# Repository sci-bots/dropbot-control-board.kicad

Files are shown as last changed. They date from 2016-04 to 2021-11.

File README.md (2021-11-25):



# DropBot v3 control board

The control board is a component of the [DropBot system][dropbot] responsible for:

* serial communication with the host computer (via USB)
* generation of the high-voltage driving signal (up to 140V @ < 10 kHz)
* impedance-measurement (for estimating drop position, velocity, etc.)
* control of other system hardware (e.g., switching boards)

For more information, please visit https://sci-bots.com

[Sci-Bots logo][sci-bots]

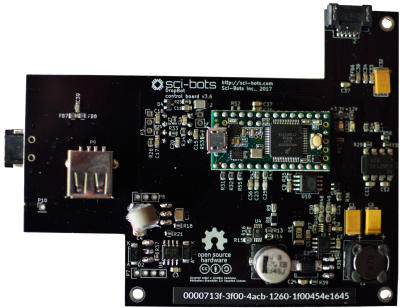
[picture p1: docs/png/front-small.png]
front

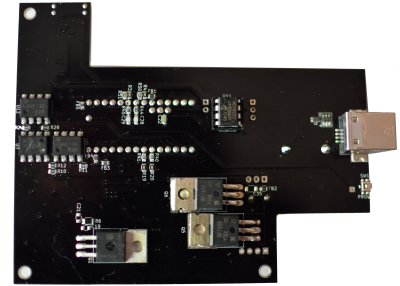
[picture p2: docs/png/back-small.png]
back


This design is open-source hardware released under a [Creative Commons Attribution-ShareAlike licence][cc-by-sa].

[][cc-by-sa]

[dropbot]: https://github.com/sci-bots/dropbot-v3
[sci-bots]: https://sci-bots.com/
[cc-by-sa]: http://creativecommons.org/licenses/by-sa/3.0

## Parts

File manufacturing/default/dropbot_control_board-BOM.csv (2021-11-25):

Refs | Quantity | MPN | Manufacturer | datasheet | footprint | value
C1 | 1 | T494D106M025AT | KEMET |  | Capacitors_Tantalum_SMD:TantalC_SizeD_EIA-7343_Reflow | 10uF
C11, C15 | 2 | CC0805KKX7R9BB105 | Yageo |  | Capacitors_SMD:C_0805 | 1uF
C12 | 1 | CL21C100JECNNWC | Samsung |  | Capacitors_SMD:C_0805 | 10pF
C13, C19-C21 | 4 | CL21C101JECNNWC | Samsung |  | Capacitors_SMD:C_0805 | 100pF
C14 | 1 | CL21C471JDFNNWG | Samsung |  | Capacitors_SMD:C_0805 | 470pF
C16 | 1 | 08053C154JAT2A | KYOCERA AVX |  | Capacitors_SMD:C_0805 | 0.15uF
C2, C3, C5, C8, C9, C17, C18, C22, C26, C33, C36-C39 | 14 | CL21B104KBCNNNC | Samsung |  | Capacitors_SMD:C_0805 | 0.1uF
C23, C25, C28-C31 | 6 | CL21C151JBANNNC | Samsung |  | Capacitors_SMD:C_0805 | 150pF
C24 | 1 | 501R15W102KV4E | Johanson |  | Capacitors_SMD:C_0805 | 1000pF
C27, C34 | 2 | CC0805KRX7R9BB103 | Yageo |  | Capacitors_SMD:C_0805 | 0.01uF
C32 | 1 | T491D336K020AT | KEMET |  | Sci-Bots:SM2917 | 33uF
C35 | 1 | DNP | DNP |  | Capacitors_SMD:C_1206 | C
C4, C10 | 2 | C1210C104KCRACTU | KEMET |  | Capacitors_SMD:C_1210 | 100n,500V
C6 | 1 | T491X107K025AT | KEMET |  | Capacitors_Tantalum_SMD:TantalC_SizeE_EIA-7360_Reflow | 100uF
C7 | 1 | EEV-EB2G3R3Q | Panasonic |  | Capacitors_SMD:c_elec_10x10 | 3.3uF,400V
D1 | 1 | VS-4EGU06-M3/5BT | Vishay |  | Diodes_SMD:SMC_Standard | 400V, 4A, <50ns
D2, D3 | 2 | US1J-13-F | Diodes Inc. |  | Diodes_SMD:SMA_Standard | D
D4 | 1 | TBAV99,LM | Toshiba |  | TO_SOT_Packages_SMD:SOT-23 | BAV99
D5 | 1 | 824015 | Würth Elektronik |  | Sci-Bots:wurth-WE-TVS_SOT23-6L | WE-TVS_824015
F1 | 1 | B59773B0120A070 | EPCOS |  | Resistors_ThroughHole:Resistor_Vertical_RM5mm | PTC
F2 | 1 | B59807A0090A062 | EPCOS |  | Resistors_SMD:R_1210 | PTC 15mA
FB1-FB8 | 8 | 742792040 | Würth Elektronik |  | Resistors_SMD:R_0805 | FERRITE
L1 | 1 | SRR1210-470M | Bourns |  | footprints:SRR1210 | 47uH,3.8A
L2 | 1 | 744231091 | Würth Elektronik |  | Sci-Bots:wurth-WE-CNSW_0805 | 90 Ohm@100MHz
LED1 | 1 | 150080BS75000 | Würth Elektronik |  | LEDs:LED_0805 | +3.3V
LED2 | 1 | 150080BS75000 | Würth Elektronik |  | LEDs:LED_0805 | +12V
P1, P2, P5 | 3 | DNP | DNP |  | Connect:1pin | CONN_01X01
P10 | 1 | DNP | DNP |  | Pin_Headers:Pin_Header_Straight_1x01_Pitch2.54mm | CONN_01X01
P11 | 1 | TFM-105-02-L-DH | Samtec |  | Sci-Bots:TFM-105-02-X-DH | TFM-105-02-X-DH
P3 | 1 | DNP | DNP |  | Pin_Headers:Pin_Header_Straight_1x03_Pitch2.54mm | CONN_01X03
P4 | 1 | DNP | DNP |  | Pin_Headers:Pin_Header_Straight_1x02_Pitch2.54mm | CONN_01X02
P6 | 1 | 1734346-1 | TE Connectivity |  | Sci-Bots:1734346-1 | USB_B
P7 | 1 | DNP | DNP |  | Pin_Headers:Pin_Header_Straight_1x04 | CONN_01X04
P8 | 1 | DNP | DNP |  | Pin_Headers:Pin_Header_Straight_1x03 | CONN_01X03
P9 | 1 | AU-Y1006 | ASSMANN WSW Components |  | Sci-Bots:AU-Y1006 | USB_A
Q1 | 1 | STP33N65M2 | STMicroelectronics |  | TO_SOT_Packages_THT:TO-220_Neutral123_Horizontal_LargePads | STP33N65M2
Q5, Q6 | 2 | IRF740BPBF | Vishay |  | TO_SOT_Packages_THT:TO-220_Neutral123_Horizontal_LargePads | IRF740BPBF
R1 | 1 | RC0805FR-071KL | Yageo |  | Resistors_SMD:R_0805 | 1k
R10, R13, R31, R32, R34-R36, R55 | 8 | RC0805FR-075K1L | Yageo |  | Resistors_SMD:R_0805 | 5.1k
R11, R12, R24, R28-R30, R54, R56 | 8 | RC0805FR-07100RL | Yageo |  | Resistors_SMD:R_0805 | 100
R14 | 1 | ERJ-6DQJ1R0V | Panasonic |  | Resistors_SMD:R_0805 | 1
R15, R17 | 2 | RC0805FR-0751KL | Yageo |  | Resistors_SMD:R_0805 | 51k
R16, R27, R33 | 3 | RC0805FR-07100KL | Yageo |  | Resistors_SMD:R_0805 | 100k
R18, R21, R37-R39 | 5 | RC0805FR-0710RL | Yageo |  | Resistors_SMD:R_0805 | 10
R23, R53 | 2 | RC0805FR-071ML | Yageo |  | Resistors_SMD:R_0805 | 1Meg
R26 | 1 | RC0805FR-072K2L | Yageo |  | Resistors_SMD:R_0805 | 2.2k
R2-R4, R19, R20 | 5 | RC0805FR-072KL | Yageo |  | Resistors_SMD:R_0805 | 2k
R40, R41, R48-R51 | 6 | RC0805FR-07150RL | Yageo |  | Resistors_SMD:R_0805 | 150
R42-R47 | 6 | RC0805FR-0751RL | Yageo |  | Resistors_SMD:R_0805 | 51
R5 | 1 | CSR2512C0R03F | Riedon |  | Resistors_SMD:R_2512 | 30m
R52 | 1 | RC0805JR-070RL | Yageo |  | Resistors_SMD:R_0805 | 0R
R6, R8, R22 | 3 | HVCB1206KDL2M00 | Stackpole Electronics |  | Resistors_SMD:R_1206 | 2M
R7 | 1 | RC0805FR-079K1L | Yageo |  | Resistors_SMD:R_0805 | 9.1k
R25 | 1 | RC0805FR-0710KL | Yageo |  | Resistors_SMD:R_0805 | 10k
R9 | 1 | RC0805FR-0720KL | Yageo |  | Resistors_SMD:R_0805 | 20k
SW1 | 1 | PTS840 GK SMTR LFS | C&K Components |  | Sci-Bots:PTS840_GK_SMTR_LFS | PROG
U1 | 1 | DNP | DNP |  | Sci-Bots:Teensy-3.2 | Teensy_3.2
U10 | 1 | IS25LP064A-JBLE | ISSI | https://www.winbond.com/resource-files/w25q64fv%20revq%2006142016.pdf | Sci-Bots:SSO-8_5.2x5.2mm_Pitch1.27mm | IS25LP064A-JBLE
U11 | 1 | ED08DT | On Shore Technology |  | Housings_DIP:DIP-8_W7.62mm | MCP6022
U2 | 1 | MAX1771ESA+ | Maxim Integrated |  | Housings_SOIC:SOIC-8_3.9x4.9mm_Pitch1.27mm | MAX1771
U3 | 1 | CAT5171TBI-50GT3 | onsemi | http://www.onsemi.com/pub_link/Collateral/CAT5171-D.PDF | Sci-Bots:SOT-23-8 | CAT5171
U4 | 1 | HV7802MG-G | Microchip |  | footprints:MSOP-8 | HV7802
U5, U7, U8, U12 | 4 | TLP227G-2(TP1,N,F) | Toshiba |  | SMD_Packages:DIP-8_SMD | DPST (2 Form A), 350V
U6 | 1 | NCP5304DR2G | onsemi |  | SMD_Packages:SOIC-8-N | NCP5304
U9 | 1 | 74AHC1G32GW,125 | Nexperia | http://www.nxp.com/documents/data_sheet/74AHC_AHCT1G32.pdf | TO_SOT_Packages_SMD:SOT-353 | 74AHC1G32

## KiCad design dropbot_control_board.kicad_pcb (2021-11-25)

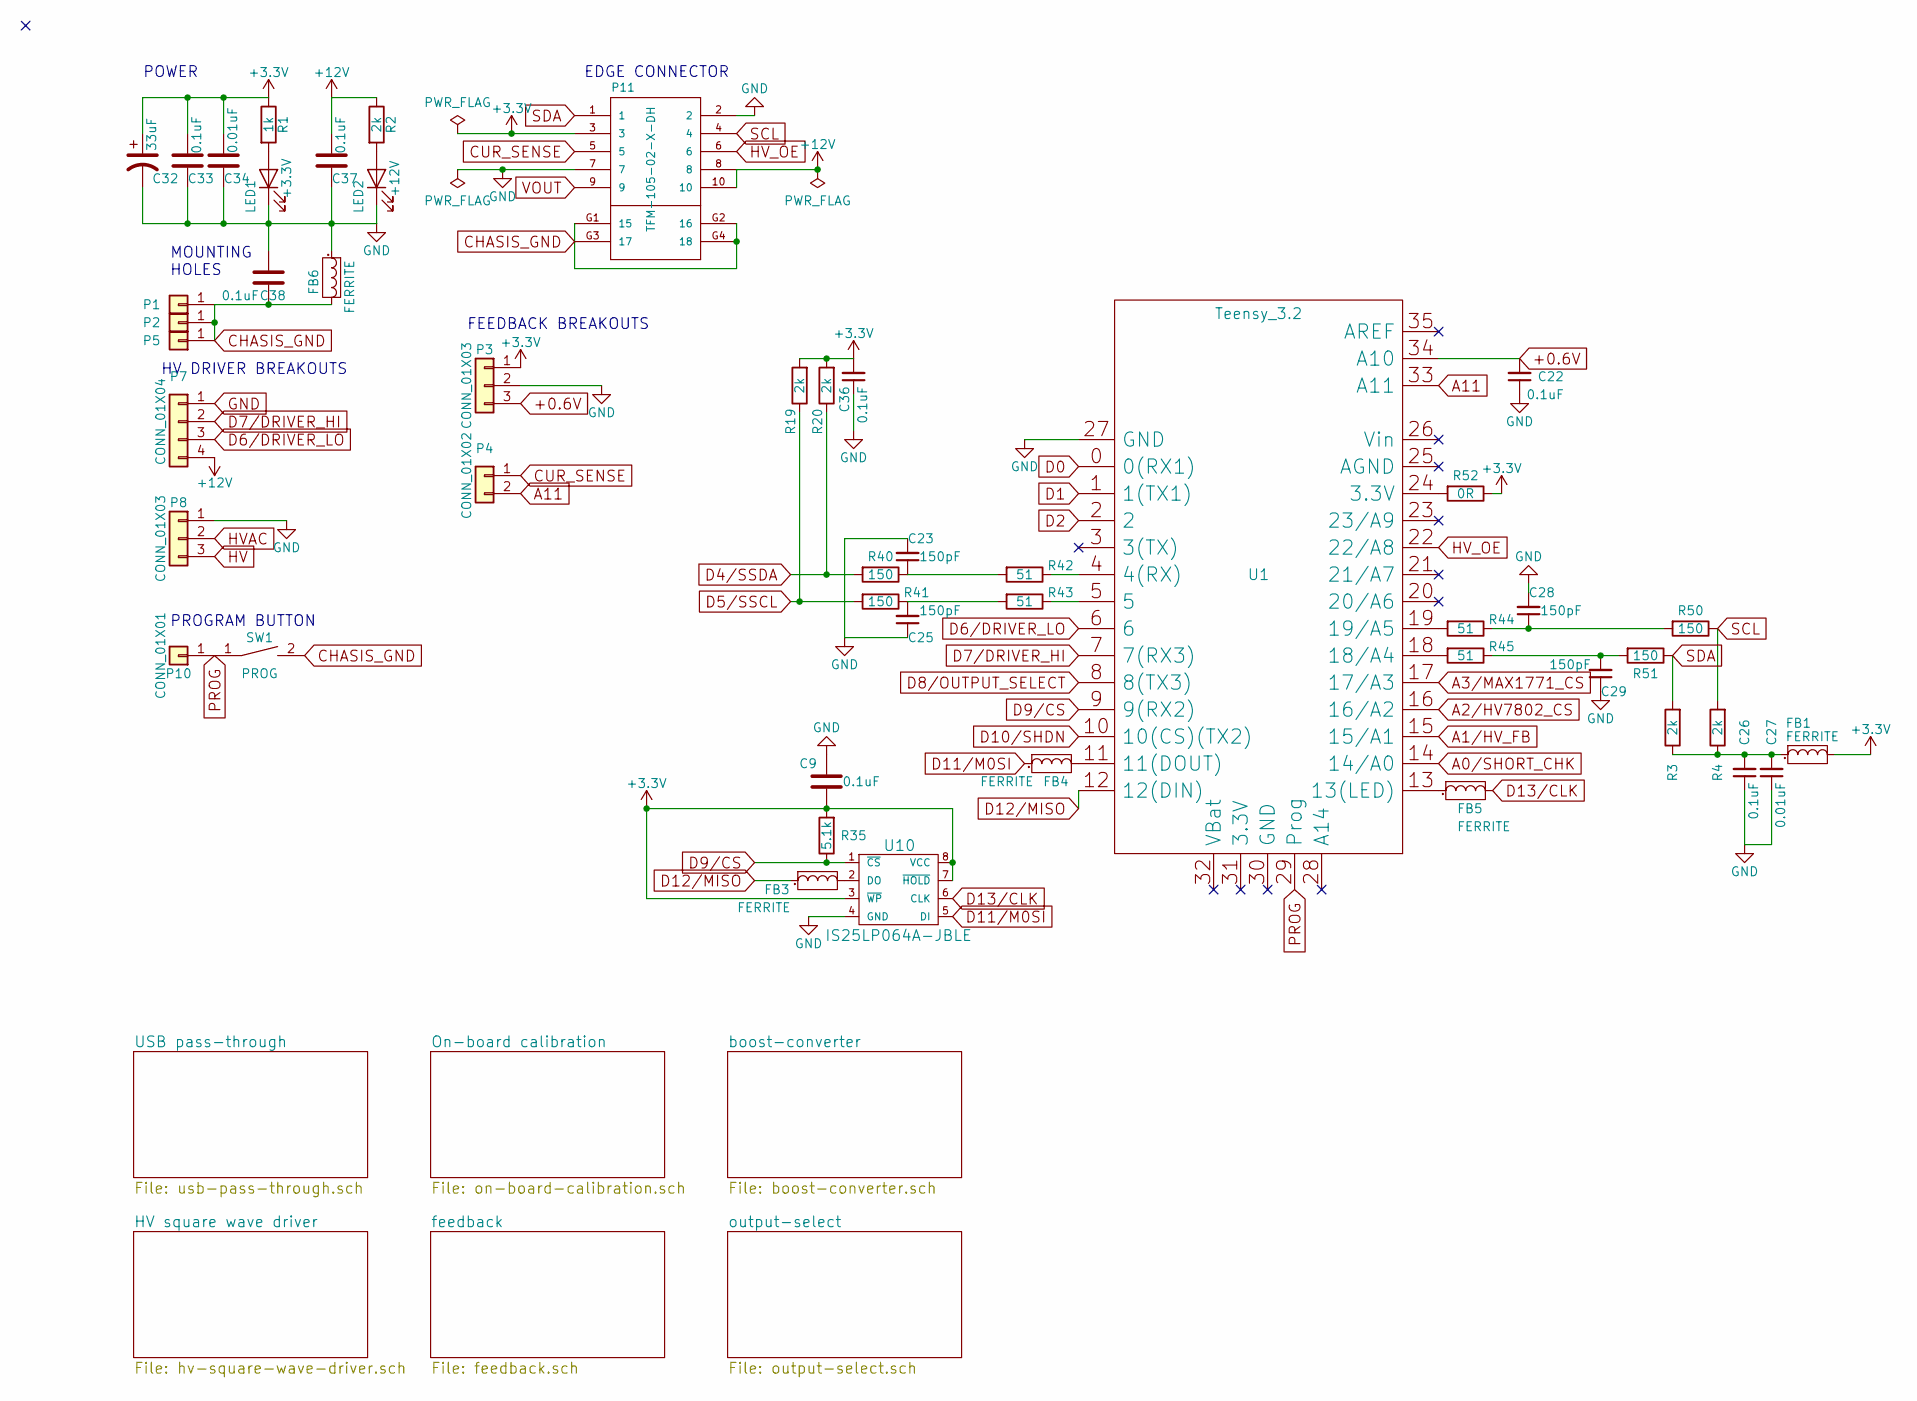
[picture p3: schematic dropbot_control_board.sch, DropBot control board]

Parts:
C9, C22, C26, C33, C36, C37, C38: 0.1uF; C_0805; MPN CL21B104KBCNNNC
C23, C25, C28, C29: 150pF; C_0805; MPN CL21C151JBANNNC
C27, C34: 0.01uF; C_0805; MPN CC0805KRX7R9BB103
C32: 33uF; SM2917; MPN T491D336K020AT
FB1, FB3, FB4, FB5, FB6: FERRITE; R_0805; MPN 742792040
LED1: +3.3V; LED_0805; MPN 150080BS75000
LED2: +12V; LED_0805; MPN 150080BS75000
P1, P2, P5: CONN_01X01; 1pin; MPN DNP
P3: CONN_01X03; Pin_Header_Straight_1x03_Pitch2.54mm; MPN DNP
P4: CONN_01X02; Pin_Header_Straight_1x02_Pitch2.54mm; MPN DNP
P7: CONN_01X04; Pin_Header_Straight_1x04; MPN DNP
P8: CONN_01X03; Pin_Header_Straight_1x03; MPN DNP
P10: CONN_01X01; Pin_Header_Straight_1x01_Pitch2.54mm; MPN DNP
P11: TFM-105-02-X-DH; MPN TFM-105-02-L-DH
R1: 1k; R_0805; MPN RC0805FR-071KL
R2, R3, R4, R19, R20: 2k; R_0805; MPN RC0805FR-072KL
R35: 5.1k; R_0805; MPN RC0805FR-075K1L
R40, R41, R50, R51: 150; R_0805; MPN RC0805FR-07150RL
R42, R43, R44, R45: 51; R_0805; MPN RC0805FR-0751RL
R52: 0R; R_0805; MPN RC0805JR-070RL
SW1: PROG; PTS840_GK_SMTR_LFS; MPN PTS840 GK SMTR LFS
U1: Teensy_3.2; Teensy-3.2; MPN DNP
U10: IS25LP064A-JBLE; SSO-8_5.2x5.2mm_Pitch1.27mm; MPN IS25LP064A-JBLE

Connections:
+0.6V: C22.2, P3.3, U1.34 (A10); also elsewhere on the board
+3V3: C9.1, C32.1, C33.2, C34.2, C36.2, FB1.2, P3.1, P11.3, R1.1, R19.2, R20.2, R35.2, R52.1, U10.3 (~WP), U10.7 (~HOLD), U10.8 (VCC); also elsewhere on the board
+12V: C37.2, P7.4, P11.8, P11.10, R2.1; also elsewhere on the board
A0/SHORT_CHK: U1.14 (14/A0); also elsewhere on the board
A1/HV_FB: U1.15 (15/A1); also elsewhere on the board
A2/HV7802_CS: U1.16 (16/A2); also elsewhere on the board
A3/MAX1771_CS: U1.17 (17/A3); also elsewhere on the board
A11: P4.2, U1.33 (A11); also elsewhere on the board
CHASIS_GND: C38.1, FB6.2, P1.1, P2.1, P5.1, P11.G1 (15), P11.G2 (16), P11.G3 (17), P11.G4 (18), SW1.2; also elsewhere on the board
CUR_SENSE: P4.1, P11.5; also elsewhere on the board
D0: U1.0 (0(RX1)); also elsewhere on the board
D1: U1.1 (1(TX1)); also elsewhere on the board
D2: U1.2; also elsewhere on the board
D4/SSDA: R20.1, R40.2; also elsewhere on the board
D5/SSCL: R19.1, R41.2; also elsewhere on the board
D6/DRIVER_LO: P7.3, U1.6; also elsewhere on the board
D7/DRIVER_HI: P7.2, U1.7 (7(RX3)); also elsewhere on the board
D8/OUTPUT_SELECT: U1.8 (8(TX3)); also elsewhere on the board
D9/CS: R35.1, U1.9 (9(RX2)), U10.1 (~CS)
D10/SHDN: U1.10 (10(CS)(TX2)); also elsewhere on the board
D11/M0SI: FB4.1, U10.5 (DI)
D12/MISO: FB3.1, U1.12 (12(DIN))
D13/CLK: FB5.2, U10.6 (CLK)
GND: C9.2, C22.1, C23.2, C25.1, C26.1, C27.1, C28.2, C29.1, C32.2, C33.1, C34.1, C36.1, C37.1, C38.2, FB6.1, LED1.1 (K), LED2.1 (K), P3.2, P7.1, P8.1, P11.2, P11.7, U1.27 (GND), U10.4 (GND); also elsewhere on the board
HV: P8.3; also elsewhere on the board
HVAC: P8.2; also elsewhere on the board
HV_OE: P11.6, U1.22 (22/A8); also elsewhere on the board
unnamed: C23.1, R40.1, R42.2
unnamed: C25.2, R41.1, R43.2
unnamed: C26.2, C27.2, FB1.1, R3.1, R4.1
unnamed: C28.1, R44.1, R50.2
unnamed: C29.2, R45.1, R51.2
unnamed: FB3.2, U10.2 (DO)
unnamed: FB4.2, U1.11 (11(DOUT))
unnamed: FB5.1, U1.13 (13(LED))
unnamed: LED1.2 (A), R1.2
unnamed: LED2.2 (A), R2.2
unnamed: R42.1, U1.4 (4(RX))
unnamed: R43.1, U1.5
unnamed: R44.2, U1.19 (19/A5)
unnamed: R45.2, U1.18 (18/A4)
unnamed: R52.2, U1.24 (3.3V)
PROG: P10.1, SW1.1, U1.29 (Prog)
SCL: P11.4, R4.2, R50.1
SDA: P11.1, R3.2, R51.1
VOUT: P11.9; also elsewhere on the board

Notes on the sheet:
EDGE CONNECTOR
HV DRIVER BREAKOUTS
FEEDBACK BREAKOUTS
MOUNTING HOLES
PROGRAM BUTTON
POWER

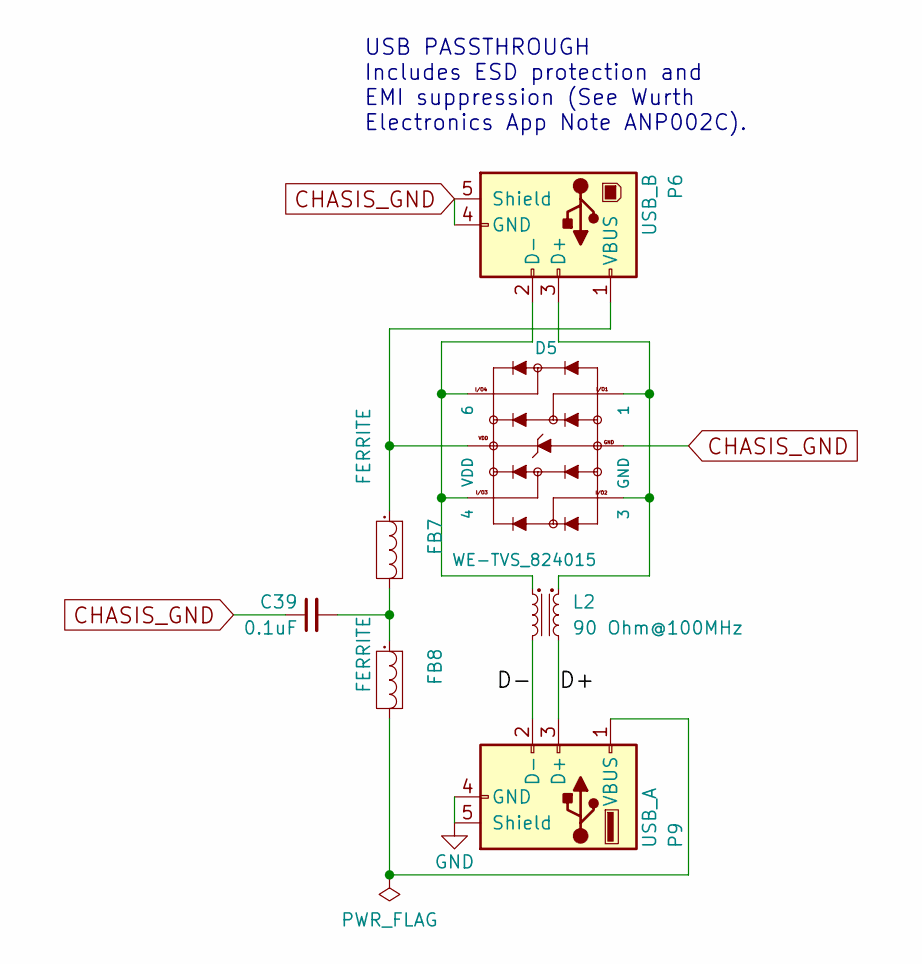
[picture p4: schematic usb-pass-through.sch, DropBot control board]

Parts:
C39: 0.1uF; C_0805; MPN CL21B104KBCNNNC
D5: WE-TVS_824015; wurth-WE-TVS_SOT23-6L; MPN 824015
FB7, FB8: FERRITE; R_0805; MPN 742792040
L2: 90 Ohm@100MHz; wurth-WE-CNSW_0805; MPN 744231091
P6: USB_B; 1734346-1; MPN 1734346-1
P9: USB_A; AU-Y1006; MPN AU-Y1006

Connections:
/USB pass-through/D+: L2.2, P9.3 (D+)
/USB pass-through/D-: L2.3, P9.2 (D-)
CHASIS_GND: C39.1, D5.2 (GND), P6.4 (GND), P6.5 (Shield); also elsewhere on the board
GND: P9.4 (GND), P9.5 (Shield); also elsewhere on the board
unnamed: C39.2, FB7.2, FB8.1
unnamed: D5.1, D5.3, L2.1, P6.3 (D+)
unnamed: D5.4, D5.6, L2.4, P6.2 (D-)
unnamed: D5.5 (VDD), FB7.1, P6.1 (VBUS)
unnamed: FB8.2, P9.1 (VBUS)

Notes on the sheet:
USB PASSTHROUGH Includes ESD protection and EMI suppression (See Wurth Electronics App Note ANP002C).

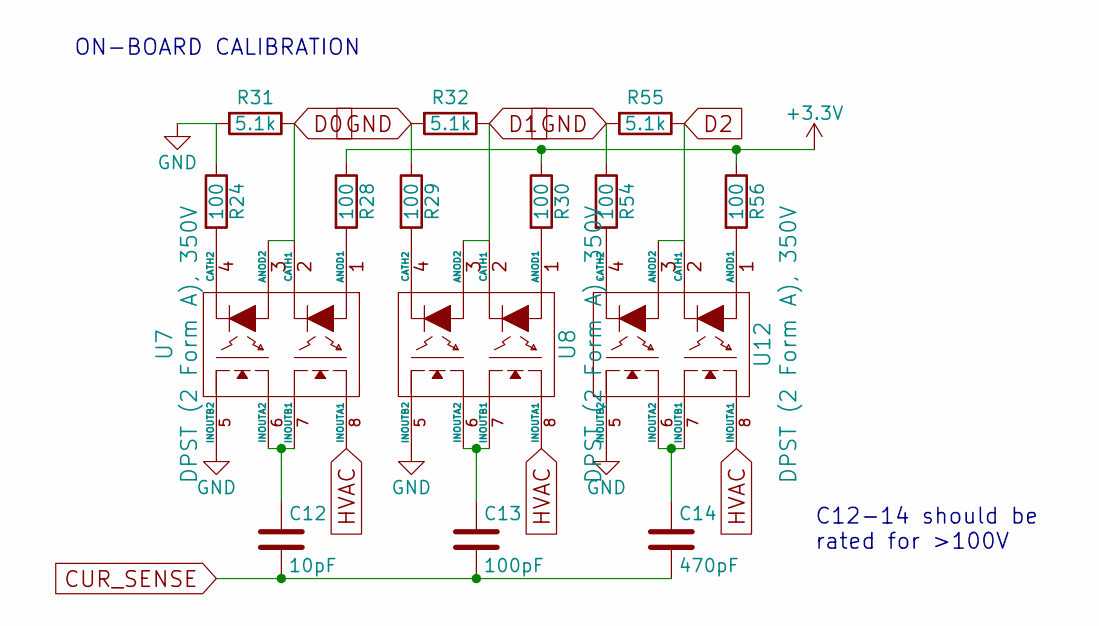
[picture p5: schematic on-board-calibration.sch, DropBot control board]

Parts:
C12: 10pF; C_0805; MPN CL21C100JECNNWC
C13: 100pF; C_0805; MPN CL21C101JECNNWC
C14: 470pF; C_0805; MPN CL21C471JDFNNWG
R24, R28, R29, R30, R54, R56: 100; R_0805; MPN RC0805FR-07100RL
R31, R32, R55: 5.1k; R_0805; MPN RC0805FR-075K1L
U7, U8, U12: DPST (2 Form A), 350V; DIP-8_SMD; MPN TLP227G-2(TP1,N,F)

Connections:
+3V3: R28.1, R30.1, R56.1; also elsewhere on the board
CUR_SENSE: C12.2, C13.2, C14.2; also elsewhere on the board
D0: R31.1, U7.2 (CATH1), U7.3 (ANOD2); also elsewhere on the board
D1: R32.1, U8.2 (CATH1), U8.3 (ANOD2); also elsewhere on the board
D2: R55.1, U12.2 (CATH1), U12.3 (ANOD2); also elsewhere on the board
GND: R24.1, R29.1, R31.2, R32.2, R54.1, R55.2, U7.5 (INOUTB2), U8.5 (INOUTB2), U12.5 (INOUTB2); also elsewhere on the board
HVAC: U7.8 (INOUTA1), U8.8 (INOUTA1), U12.8 (INOUTA1); also elsewhere on the board
unnamed: C12.1, U7.6 (INOUTA2), U7.7 (INOUTB1)
unnamed: C13.1, U8.6 (INOUTA2), U8.7 (INOUTB1)
unnamed: C14.1, U12.6 (INOUTA2), U12.7 (INOUTB1)
unnamed: R24.2, U7.4 (CATH2)
unnamed: R28.2, U7.1 (ANOD1)
unnamed: R29.2, U8.4 (CATH2)
unnamed: R30.2, U8.1 (ANOD1)
unnamed: R54.2, U12.4 (CATH2)
unnamed: R56.2, U12.1 (ANOD1)

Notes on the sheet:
ON-BOARD CALIBRATION
C12-14 should be rated for >100V

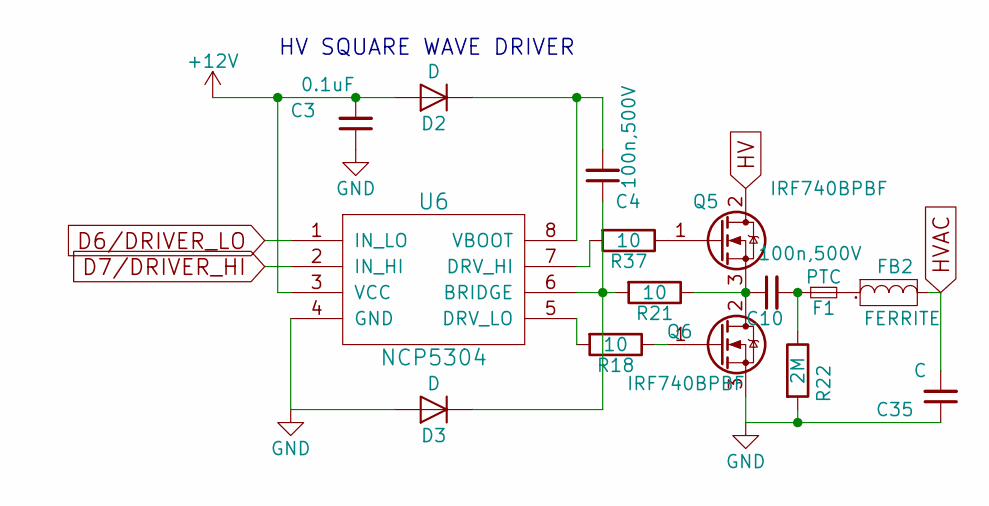
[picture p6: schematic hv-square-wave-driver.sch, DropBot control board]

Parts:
C3: 0.1uF; C_0805; MPN CL21B104KBCNNNC
C4, C10: 100n,500V; C_1210; MPN C1210C104KCRACTU
C35: C; C_1206; MPN DNP
D2, D3: D; SMA_Standard; MPN US1J-13-F
F1: PTC; Resistor_Vertical_RM5mm; MPN B59773B0120A070
FB2: FERRITE; R_0805; MPN 742792040
Q5, Q6: IRF740BPBF; TO-220_Neutral123_Horizontal_LargePads; MPN IRF740BPBF
R18, R21, R37: 10; R_0805; MPN RC0805FR-0710RL
R22: 2M; R_1206; MPN HVCB1206KDL2M00
U6: NCP5304; SOIC-8-N; MPN NCP5304DR2G

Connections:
+12V: C3.2, D2.2 (A), U6.3 (VCC); also elsewhere on the board
D6/DRIVER_LO: U6.1 (IN_LO); also elsewhere on the board
D7/DRIVER_HI: U6.2 (IN_HI); also elsewhere on the board
GND: C3.1, C35.1, D3.2 (A), Q6.3 (S), R22.2, U6.4 (GND); also elsewhere on the board
HV: Q5.2 (D); also elsewhere on the board
HVAC: C35.2, FB2.2; also elsewhere on the board
unnamed: C4.1, D3.1 (K), R21.2, U6.6 (BRIDGE)
unnamed: C4.2, D2.1 (K), U6.8 (VBOOT)
unnamed: C10.1, Q5.3 (S), Q6.2 (D), R21.1
unnamed: C10.2, F1.1, R22.1
unnamed: F1.2, FB2.1
unnamed: Q5.1 (G), R37.1
unnamed: Q6.1 (G), R18.1
unnamed: R18.2, U6.5 (DRV_LO)
unnamed: R37.2, U6.7 (DRV_HI)

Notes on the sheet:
HV SQUARE WAVE DRIVER

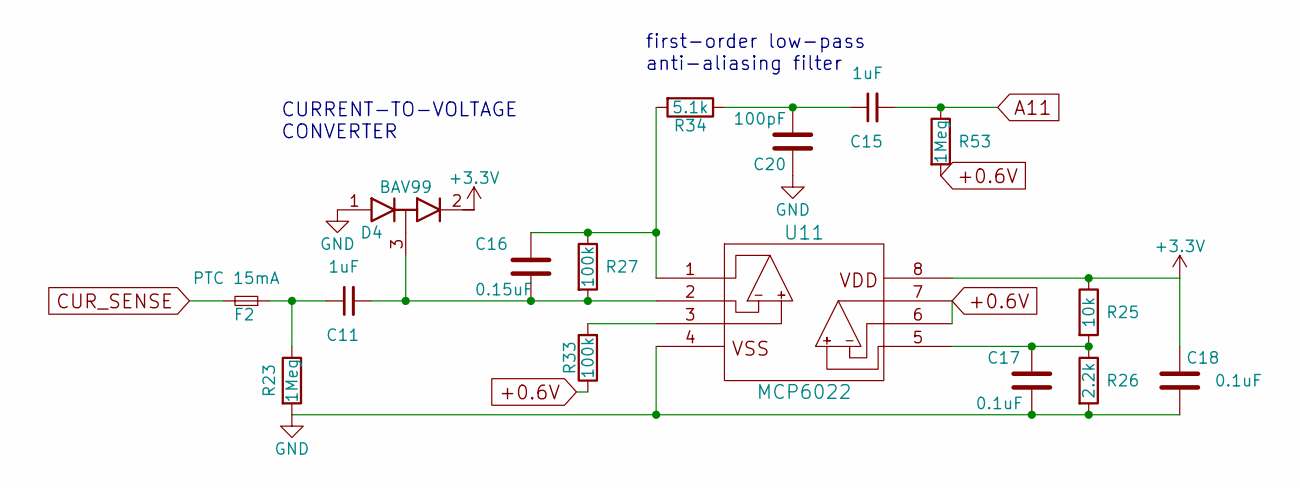
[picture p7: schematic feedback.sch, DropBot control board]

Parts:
C11, C15: 1uF; C_0805; MPN CC0805KKX7R9BB105
C16: 0.15uF; C_0805; MPN 08053C154JAT2A
C17, C18: 0.1uF; C_0805; MPN CL21B104KBCNNNC
C20: 100pF; C_0805; MPN CL21C101JECNNWC
D4: BAV99; SOT-23; MPN TBAV99,LM
F2: PTC 15mA; R_1210; MPN B59807A0090A062
R23, R53: 1Meg; R_0805; MPN RC0805FR-071ML
R25: 10k; R_0805; MPN RC0805FR-0710KL
R26: 2.2k; R_0805; MPN RC0805FR-072K2L
R27, R33: 100k; R_0805; MPN RC0805FR-07100KL
R34: 5.1k; R_0805; MPN RC0805FR-075K1L
U11: MCP6022; DIP-8_W7.62mm; MPN ED08DT

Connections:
+0.6V: R33.1, R53.2, U11.6 (VINB-), U11.7 (VOUTB); also elsewhere on the board
+3V3: C18.1, D4.2 (K), R25.1, U11.8 (VDD); also elsewhere on the board
A11: C15.2, R53.1; also elsewhere on the board
CUR_SENSE: F2.2; also elsewhere on the board
GND: C17.2, C18.2, C20.1, D4.1 (A), R23.2, R26.2, U11.4 (VSS); also elsewhere on the board
unnamed: C11.1, F2.1, R23.1
unnamed: C11.2, C16.2, D4.3 (common), R27.2, U11.2 (VINA-)
unnamed: C15.1, C20.2, R34.1
unnamed: C16.1, R27.1, R34.2, U11.1 (VOUTA)
unnamed: C17.1, R25.2, R26.1, U11.5 (VINB+)
unnamed: R33.2, U11.3 (VINA+)

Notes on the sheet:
first-order low-pass anti-aliasing filter
CURRENT-TO-VOLTAGE CONVERTER

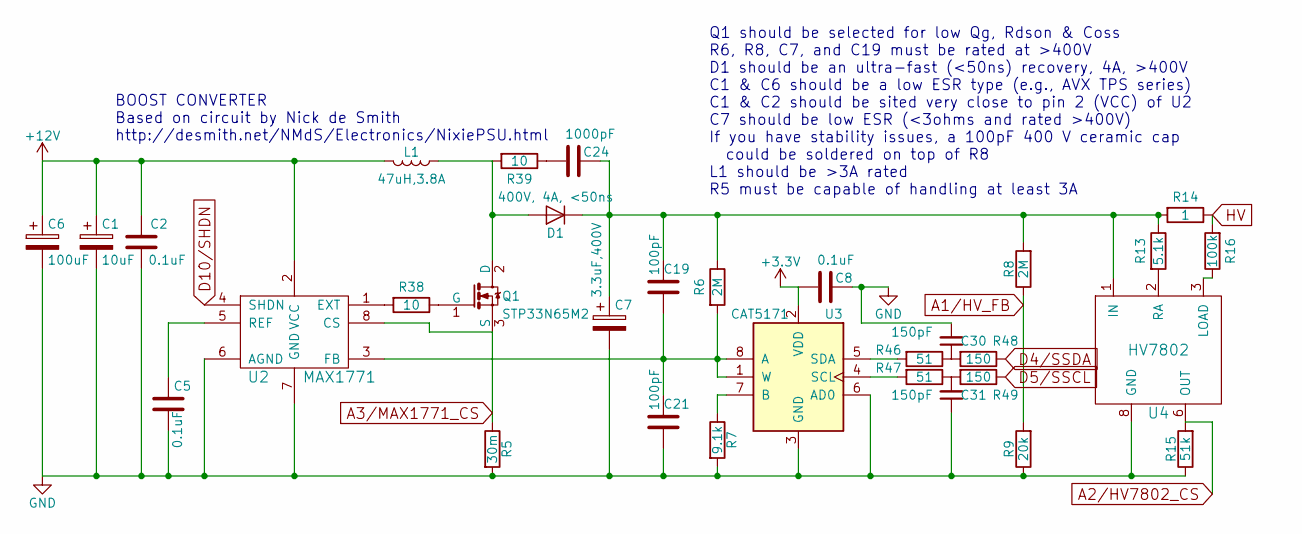
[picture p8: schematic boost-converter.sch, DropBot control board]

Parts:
C1: 10uF; TantalC_SizeD_EIA-7343_Reflow; MPN T494D106M025AT
C2, C5, C8: 0.1uF; C_0805; MPN CL21B104KBCNNNC
C6: 100uF; TantalC_SizeE_EIA-7360_Reflow; MPN T491X107K025AT
C7: 3.3uF,400V; c_elec_10x10; MPN EEV-EB2G3R3Q
C19, C21: 100pF; C_0805; MPN CL21C101JECNNWC
C24: 1000pF; C_0805; MPN 501R15W102KV4E
C30, C31: 150pF; C_0805; MPN CL21C151JBANNNC
D1: 400V, 4A, <50ns; SMC_Standard; MPN VS-4EGU06-M3/5BT
L1: 47uH,3.8A; SRR1210; MPN SRR1210-470M
Q1: STP33N65M2; TO-220_Neutral123_Horizontal_LargePads; MPN STP33N65M2
R5: 30m; R_2512; MPN CSR2512C0R03F
R6, R8: 2M; R_1206; MPN HVCB1206KDL2M00
R7: 9.1k; R_0805; MPN RC0805FR-079K1L
R9: 20k; R_0805; MPN RC0805FR-0720KL
R13: 5.1k; R_0805; MPN RC0805FR-075K1L
R14: 1; R_0805; MPN ERJ-6DQJ1R0V
R15: 51k; R_0805; MPN RC0805FR-0751KL
R16: 100k; R_0805; MPN RC0805FR-07100KL
R38, R39: 10; R_0805; MPN RC0805FR-0710RL
R46, R47: 51; R_0805; MPN RC0805FR-0751RL
R48, R49: 150; R_0805; MPN RC0805FR-07150RL
U2: MAX1771; SOIC-8_3.9x4.9mm_Pitch1.27mm; MPN MAX1771ESA+
U3: CAT5171; SOT-23-8; MPN CAT5171TBI-50GT3
U4: HV7802; MSOP-8; MPN HV7802MG-G

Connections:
+3V3: C8.2, U3.2 (VDD); also elsewhere on the board
+12V: C1.1, C2.2, C6.1, L1.2, U2.2 (VCC); also elsewhere on the board
A1/HV_FB: R8.1, R9.2; also elsewhere on the board
A2/HV7802_CS: R15.2, U4.6 (OUT); also elsewhere on the board
A3/MAX1771_CS: Q1.3 (S), R5.1, U2.8 (CS); also elsewhere on the board
D4/SSDA: R48.1; also elsewhere on the board
D5/SSCL: R49.1; also elsewhere on the board
D10/SHDN: U2.4 (SHDN); also elsewhere on the board
GND: C1.2, C2.1, C5.2, C6.2, C7.2, C8.1, C21.1, C30.2, C31.1, R5.2, R7.2, R9.1, R15.1, U2.6 (AGND), U2.7 (GND), U3.3 (GND), U3.6 (AD0), U4.8 (GND); also elsewhere on the board
HV: R14.1, R16.2; also elsewhere on the board
unnamed: C5.1, U2.5 (REF)
unnamed: C19.1, C21.2, R6.2, U2.3 (FB), U3.1 (W), U3.8 (A)
unnamed: C7.1, C19.2, C24.1, D1.1 (K), R6.1, R8.2, R13.1, R14.2, U4.1 (IN)
unnamed: C24.2, R39.1
unnamed: C30.1, R46.1, R48.2
unnamed: C31.2, R47.1, R49.2
unnamed: D1.2 (A), L1.1, Q1.2 (D), R39.2
unnamed: Q1.1 (G), R38.1
unnamed: R7.1, U3.7 (B)
unnamed: R13.2, U4.2 (RA)
unnamed: R16.1, U4.3 (LOAD)
unnamed: R38.2, U2.1 (EXT)
unnamed: R46.2, U3.5 (SDA)
unnamed: R47.2, U3.4 (SCL)

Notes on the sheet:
BOOST CONVERTER Based on circuit by Nick de Smith http://desmith.net/NMdS/Electronics/NixiePSU.html
Q1 should be selected for low Qg, Rdson & Coss R6, R8, C7, and C19 must be rated at >400V D1 should be an ultra-fast (<50ns) recovery, 4A, >400V C1 & C6 should be a low ESR type (e.g., AVX TPS series) C1 & C2 should be sited very close to pin 2 (VCC) of U2 C7 should be low ESR (<3ohms and rated >40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

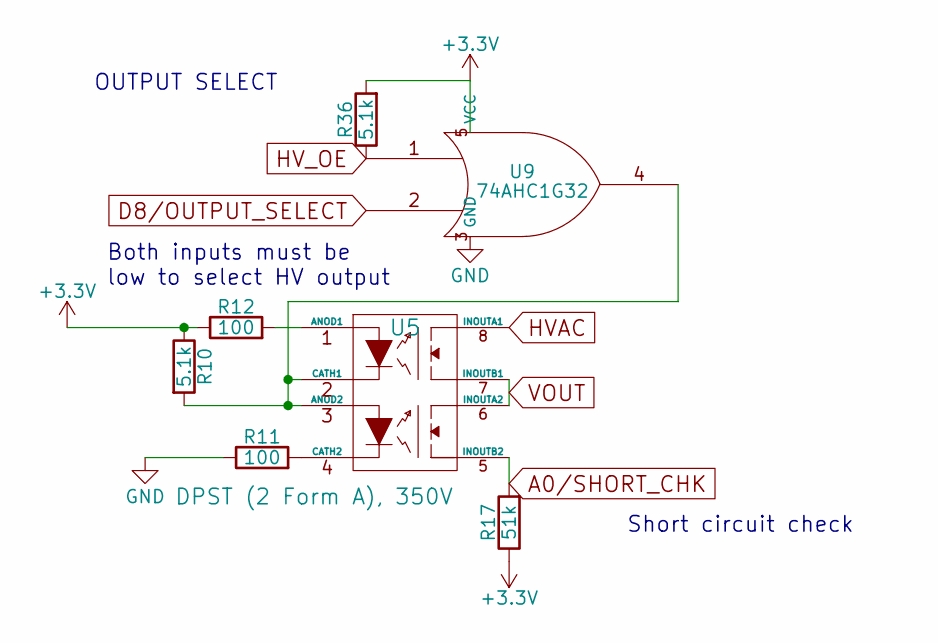
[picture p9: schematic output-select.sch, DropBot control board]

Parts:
R10, R36: 5.1k; R_0805; MPN RC0805FR-075K1L
R11, R12: 100; R_0805; MPN RC0805FR-07100RL
R17: 51k; R_0805; MPN RC0805FR-0751KL
U5: DPST (2 Form A), 350V; DIP-8_SMD; MPN TLP227G-2(TP1,N,F)
U9: 74AHC1G32; SOT-353; MPN 74AHC1G32GW,125

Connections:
+3V3: R10.1, R12.1, R17.1, R36.2, U9.5 (VCC); also elsewhere on the board
A0/SHORT_CHK: R17.2, U5.5 (INOUTB2); also elsewhere on the board
D8/OUTPUT_SELECT: U9.2; also elsewhere on the board
GND: R11.1, U9.3 (GND); also elsewhere on the board
HVAC: U5.8 (INOUTA1); also elsewhere on the board
HV_OE: R36.1, U9.1; also elsewhere on the board
unnamed: R10.2, U5.2 (CATH1), U5.3 (ANOD2), U9.4
unnamed: R11.2, U5.4 (CATH2)
unnamed: R12.2, U5.1 (ANOD1)
VOUT: U5.6 (INOUTA2), U5.7 (INOUTB1); also elsewhere on the board

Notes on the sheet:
OUTPUT SELECT
Both inputs must be low to select HV output
Short circuit check

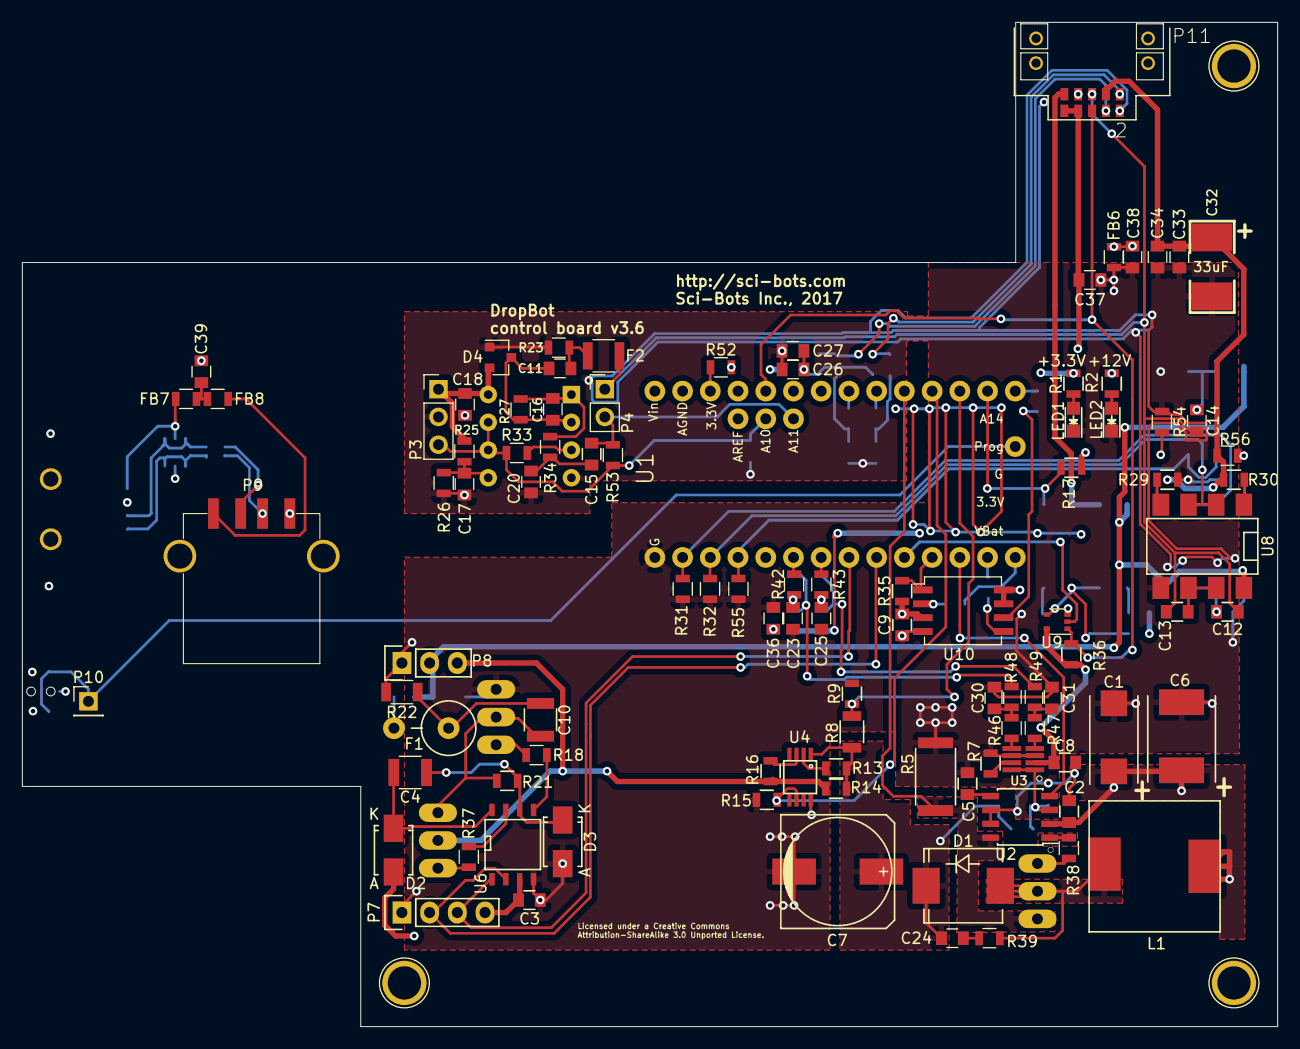
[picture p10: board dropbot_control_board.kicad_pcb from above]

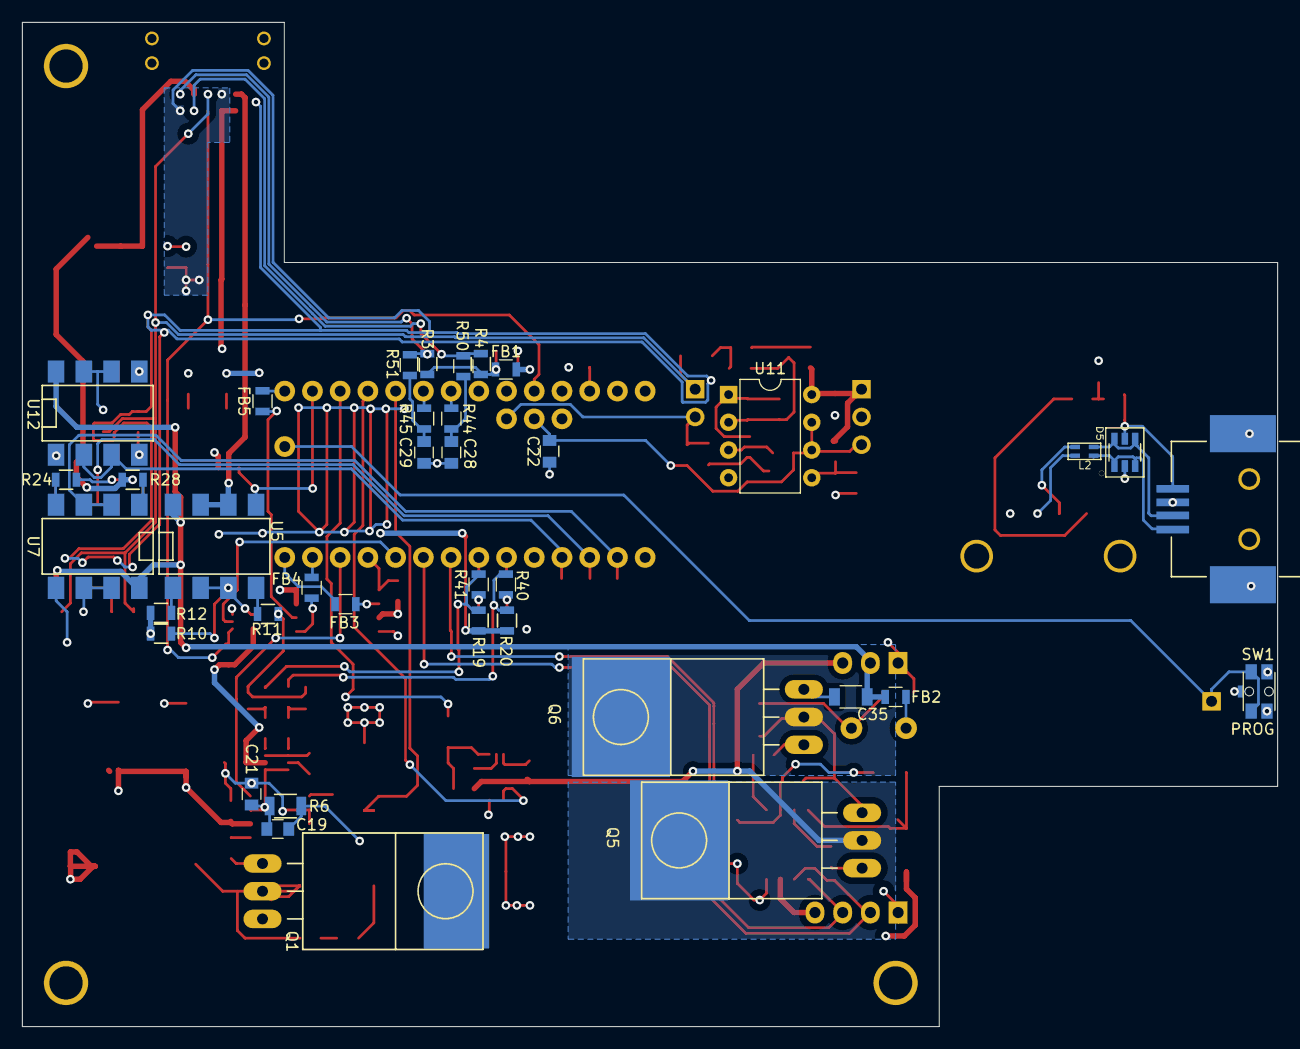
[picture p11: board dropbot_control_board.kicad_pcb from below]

Board: 4 copper layers, 115.0 x 92.0 mm, 141 parts (38 on the bottom side), 94 nets.

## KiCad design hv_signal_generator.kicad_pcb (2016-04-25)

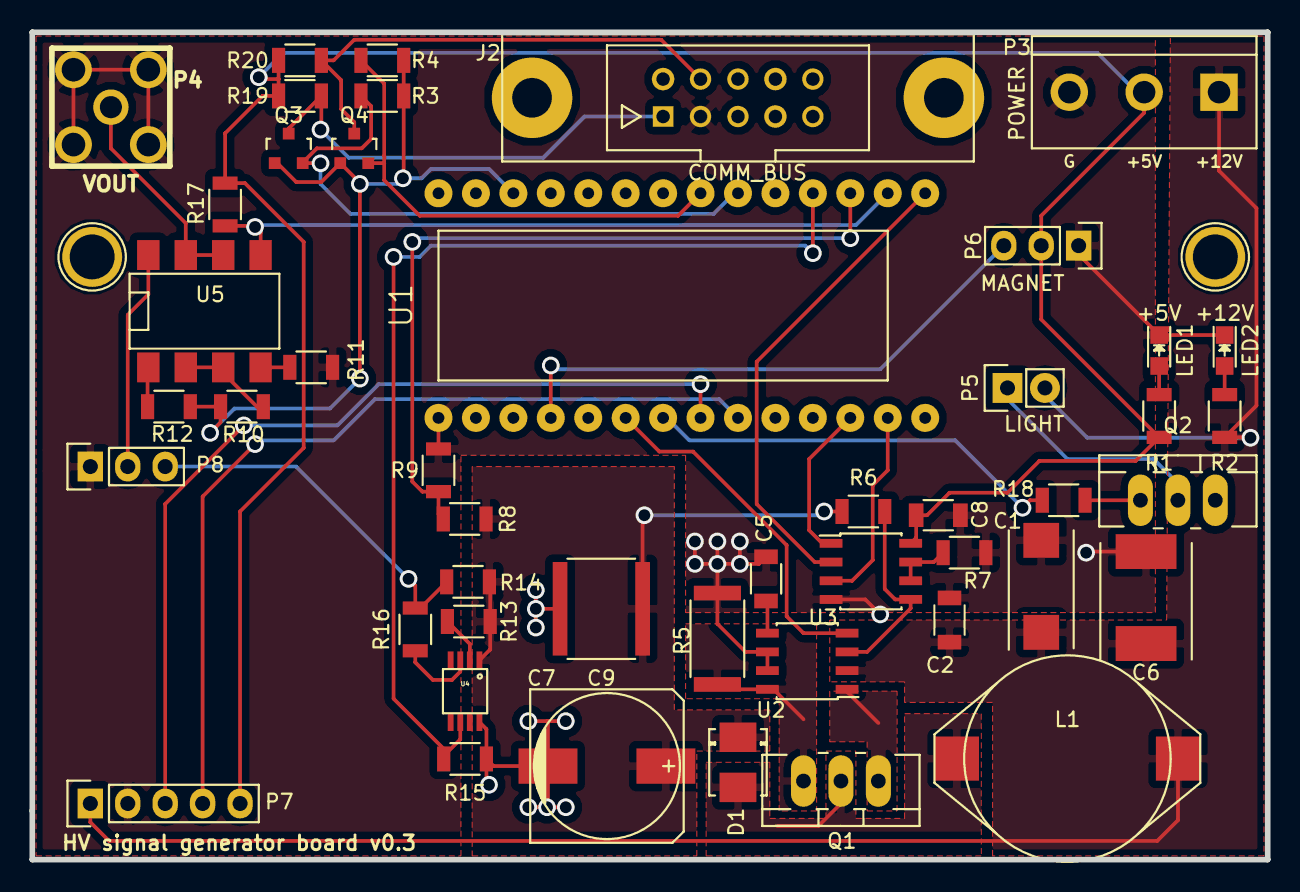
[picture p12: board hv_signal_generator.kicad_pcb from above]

Board: 2 copper layers, 83.8 x 56.1 mm, 47 parts (0 on the bottom side), 38 nets.

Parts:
C1: 10uF; TantalC_SizeD_EIA-7343_Reflow
C2, C5, C8: 0.1uF; C_1206
C6: 100uF,35V; TantalC_SizeE_EIA-7360_Reflow
C7: 3.3uF,400V; c_elec_10x10
C9: 100nF,400V; C_2225
D1: ES2F; DO-214BA
J2: COMM_BUS; he10-10d
L1: 100uH; DU1971
LED1: +5V; LED_0805
LED2: +12V; LED_0805
P3: POWER; bornier3
P4: VOUT; JACK_SMA
P5: LIGHT; Pin_Header_Straight_1x02
P6: MAGNET; Pin_Header_Straight_1x03
P7: CONN_01X05; Pin_Header_Straight_1x05
P8: CONN_01X03; Pin_Header_Straight_1x03
Q1: IRF644PBF; TO-220_Neutral123_Vertical_LargePads
Q2: TIP120; TO-220_Neutral123_Vertical_LargePads
Q3, Q4: 2N7002; SOT-23
R1, R18: 1k; R_1206
R2: 2k; R_1206
R3, R4, R13, R19, R20: 5.1k; R_1206
R5: 50m; R_2512
R6, R8: 1M; R_1206
R7: 4k; R_1206
R9: 20k; R_1206
R10: 4.75k; R_1206
R11, R12: 200; R_1206
R14: 5.1; R_1206
R15, R17: 51k; R_1206
R16: 100k; R_1206
U1: Teensy_3.1; Teensy-3.1
U2: MAX1771; SOIC-8_3.9x4.9mm_Pitch1.27mm
U3: MCP41050; SOIC-8_3.9x4.9mm_Pitch1.27mm
U4: HV7802; MSOP-8
U5: AQW216; DIP-8_SMD

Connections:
+3.3V: Q3.1, Q4.1, R3.1, R4.1, R10.1, R12.2, U1.24
+5V: C8.2, P3.2, P6.2, P7.5, R1.1, R17.1, R19.1, R20.1, U3.8
+12V: C1.1, C2.1, C6.1, L1.2, P3.1, P5.2, P7.1, R2.1, U2.2
A0/SHORT_CHK: R17.2, U1.14, U5.5
A1/HV_FB: R8.1, R9.2, U1.15
A2/CURRENT_SENSE: R15.2, U1.16, U4.6
A3/OUTPUT_SELECT: R10.2, U5.2, U5.3
D2/SERVO: P6.3, U1.2
D4/SHDN: U1.4, U2.4
D5/LED: R18.2, U1.5
D6/DRIVER_HI: P7.3, U1.6
D7/DRIVER_LO: P7.4, U1.7
D10/MCP41050_CS: U1.10, U3.1
D11/MOSI: U1.11, U3.3
D13/SCK: U1.13, U3.2
GND: C1.2, C2.2, C5.2, C6.2, C7.2, C8.1, C9.2, J2.3, LED1.1, LED2.1, P3.3, P4.2, P6.1, P7.2, P8.1, Q2.3, R5.2, R7.2, R9.1, R11.1, R15.1, U1.27, U2.6, U2.7, U3.4, U4.8
HV: P8.3, R14.1, R16.2
unnamed: C5.1, U2.5
unnamed: C7.1, C9.1, D1.1, R6.1, R8.2, R13.1, R14.2, U4.1
unnamed: D1.2, L1.1, Q1.2
unnamed: LED1.2, R1.2
unnamed: LED2.2, R2.2
unnamed: P4.1, U5.6, U5.7
unnamed: P5.1, Q2.2
unnamed: Q1.1, U2.1
unnamed: Q1.3, R5.1, U2.8
unnamed: Q2.1, R18.1
unnamed: R6.2, U2.3, U3.5
unnamed: R7.1, U3.6, U3.7
unnamed: R11.2, U5.4
unnamed: R12.1, U5.1
unnamed: R13.2, U4.2
unnamed: R16.1, U4.3
SCL_3.3V: Q4.2, R4.2, U1.19
SCL_5V: J2.4, Q4.3, R20.2
SDA_3.3V: Q3.2, R3.2, U1.18
SDA_5V: J2.1, Q3.3, R19.2
VOUT: P8.2, U5.8

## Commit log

2016-02-17 Complete layout
    [hv_signal_generator-B.Mask.gbs, hv_signal_generator-B.Paste.gbp, hv_signal_generator-B.SilkS.gbo, hv_signal_generator-Back.gbl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]
2016-02-17 Move C1 and C2 closer to MAX1771 chip and ...
    Add layout notes
    [hv_signal_generator-B.Mask.gbs, hv_signal_generator-B.Paste.gbp, hv_signal_generator-B.SilkS.gbo, hv_signal_generator-Back.gbl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]
2016-02-17 Add clearance between VOUT pin and screw
    [hv_signal_generator-B.Mask.gbs, hv_signal_generator-B.Paste.gbp, hv_signal_generator-B.SilkS.gbo, hv_signal_generator-Back.gbl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]
2016-02-18 Add part numbers to schematic`
    [hv_signal_generator-B.Mask.gbs, hv_signal_generator-B.Paste.gbp, hv_signal_generator-B.SilkS.gbo, hv_signal_generator-BOM.csv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]
2016-04-13 [WIP] Remove HV513, fix orientation of FTDI header
    * fix footprint of L1
    [hv_signal_generator-B.Mask.gbs, hv_signal_generator-B.Paste.gbp, hv_signal_generator-B.SilkS.gbo, hv_signal_generator-Back.gbl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]
2016-04-15 [WIP] Add hv signal generator breakout headers
    [hv_signal_generator-B.Mask.gbs, hv_signal_generator-B.Paste.gbp, hv_signal_generator-B.SilkS.gbo, hv_signal_generator-Back.gbl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]
2016-04-15 Swap parts to support up to 400V and use BJT for LED
    [hv_signal_generator-B.Mask.gbs, hv_signal_generator-B.Paste.gbp, hv_signal_generator-B.SilkS.gbo, hv_signal_generator-Back.gbl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]
2016-04-16 Swap ATMEGA328 for Teensy
    [hv_signal_generator-B.Mask.gbs, hv_signal_generator-B.Paste.gbp, hv_signal_generator-B.SilkS.gbo, hv_signal_generator-Back.gbl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]
2016-04-16 Suppress leading zeros in drill file
    [hv_signal_generator.drl]
2016-04-25 Replace footprint for transistors with SOT-23
    [hv_signal_generator-B.Mask.gbs, hv_signal_generator-B.Paste.gbp, hv_signal_generator-B.SilkS.gbo, hv_signal_generator-Back.gbl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]
2016-09-20 Rename dropbot-control-board
    [dropbot_control_board-BOM.csv, dropbot_control_board.kicad_pcb, dropbot_control_board.sch, hv_signal_generator.sch]
2016-09-21 Fix routing of D3/OUTPUT_SELECT and add MAX1771...
    Fix routing of D3/OUTPUT_SELECT and add MAX1771 current sensing.
    [dropbot_control_board.kicad_pcb, dropbot_control_board.sch]
2016-09-21 Connect 5V pin on COMM_BUS
    [dropbot_control_board.kicad_pcb, dropbot_control_board.sch]
2016-09-21 [WIP] Integrate HV square-wave driver (not routed)
    [dropbot_control_board.kicad_pcb, dropbot_control_board.sch]
2016-09-21 [WIP] Add feedback circuit and on-board calibration
    [dropbot_control_board.sch]
2016-09-22 Re-do layout
    [dropbot_control_board-B.Mask.gbs, dropbot_control_board-B.Paste.gbp, dropbot_control_board-B.SilkS.gbo, dropbot_control_board-Back.gbl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]
2016-09-25 Bump library version
    [dropbot_control_board.kicad_pcb]
2016-11-23 Minor fixes
    * fix inductor footprint
    * footprints for various HV resistors
    * labels for some resistors/caps
    * remove shorted +12V trace
    [dropbot_control_board-B.Mask.gbs, dropbot_control_board-B.Paste.gbp, dropbot_control_board-B.SilkS.gbo, dropbot_control_board-BOM.csv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]
2016-12-19 Use edge connectors and ...
    * Add SPI flash memory
    * Add HV output enable
    * Make feedback circuit breakout and use DIP op-amp
    * Pass Teensy's USB signals through edge connector
    [dropbot_control_board-B.Mask.gbs, dropbot_control_board-B.Paste.gbp, dropbot_control_board-B.SilkS.gbo, dropbot_control_board-Back.gbl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]
2017-01-05 Update BOM
    [dropbot_control_board.sch, dropbot_control_board_BOM.csv]
2017-01-05 Fix BOM
    [dropbot_control_board.sch, dropbot_control_board_BOM.csv]
2017-01-05 Fix op-amp package in BOM
    [dropbot_control_board.sch, dropbot_control_board_BOM.csv]
2017-03-07 EMC related improvements
    * convert to 4-layer board
    * add jumper to connect 3.3V of Teensy
    * put filters on i2c
    * add guard traces around i2c and current-sense lines
    * add ferrites to SPI lines
    * add snubber on SPMS diode
    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
    [dropbot_control_board-B.Mask.gbs, dropbot_control_board-B.Paste.gbp, dropbot_control_board-B.SilkS.gbo, dropbot_control_board-Back.gbl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]
2017-03-16 Lower the resistance of i2c pullups (4.75k --> 2k)
    [dropbot_control_board.sch, dropbot_control_board_BOM.csv]
2017-03-21 Add usb passthrough, reset button, ...
    * add usb passthrough
    * add reset button
    * fix bad trace on U5
    * fix part number for C7 (3.3uF instead of 10uF)
    [dropbot_control_board-B.Mask.gbs, dropbot_control_board-B.Paste.gbp, dropbot_control_board-B.SilkS.gbo, dropbot_control_board-Back.gbl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]
2017-04-04 Swap F2 for higher voltage rating, monitor HV_OE
    * swap F2 for 1210 footprint: B59807A90A62 (higher voltage rating)
    * monitor HV_OE with A8
    [dropbot_control_board-B.Mask.gbs, dropbot_control_board-B.Paste.gbp, dropbot_control_board-B.SilkS.gbo, dropbot_control_board-Back.gbl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]
2017-04-05 Change part numbers for i2c filters
    [dropbot_control_board-B.Mask.gbs, dropbot_control_board-B.Paste.gbp, dropbot_control_board-B.SilkS.gbo, dropbot_control_board-Back.gbl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]
2017-04-18 Update BOM with alternate parts for C6 and D4
    These parts were out of stock at Digi-key as of 2017-04-18.
    [dropbot_control_board.sch, dropbot_control_board_BOM.csv]
2017-04-20 Update current limit on F2
    [dropbot_control_board.sch, dropbot_control_board_BOM.csv]
2017-04-21 Change component for D1
    [dropbot_control_board.sch, dropbot_control_board_BOM.csv]
2017-04-25 [WIP] Fix USB-B footprint (P6)
    Fixes #3
    [dropbot_control_board.kicad_pcb]
2017-04-25 [WIP] Fixes #1: C18 is disconnected
    [dropbot_control_board.kicad_pcb, dropbot_control_board.sch]
2017-04-25 [WIP] Fixes #2: Change prefixes for J1 and IC1
    [dropbot_control_board.kicad_pcb, dropbot_control_board.sch, dropbot_control_board_BOM.csv]
2017-04-25 [WIP] Silkscreen fixes (Fixes #4)
    [dropbot_control_board.kicad_pcb]
2017-04-25 Move USB-B and program switch up 1mm
    [dropbot_control_board.kicad_pcb]
2017-04-25 Update outputs and metadata for v3.4
    [dropbot_control_board-B.Mask.gbs, dropbot_control_board-B.Paste.gbp, dropbot_control_board-B.SilkS.gbo, dropbot_control_board-Back.gbl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]
2017-05-17 Fix feedback and on-board calibration and move USB
    [boost-converter.sch, dropbot_control_board-B.Mask.gbs, dropbot_control_board-B.Paste.gbp, dropbot_control_board-B.SilkS.gbo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]
2017-06-02 Add missing schematic diagrams and change some part numbers
    [boost-converter.sch, dropbot_control_board-B.Mask.gbs, dropbot_control_board-B.Paste.gbp, dropbot_control_board-B.SilkS.gbo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]
2017-06-05 Change part number for ferrites, add *.pos files
    [boost-converter.sch, dropbot_control_board.kicad_pcb, dropbot_control_board.sch, dropbot_control_board_BOM.csv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]
2017-06-19 Improve layout/stability of boost converter, etc.
    * improve layout/stability of boost converter
    * enable on board calibration without HVOE
    * add decoupling cap to 0.6V reference
    * fix footprint for U10
    * add programming wire
    [boost-converter.sch, dropbot_control_board-B.Mask.gbs, dropbot_control_board-B.Paste.gbp, dropbot_control_board-B.SilkS.gbo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]
2017-08-09 Change value of R7 to 10k
    Fixes #6
    [boost-converter.sch, dropbot_control_board_BOM.csv]
2017-08-09 Change EEPROM and swap 150 Ohm resisotors for 100...
    Change EEPROM and swap 150 Ohm resisotors for 100 resistors
    driving the PhotoMOS switches.
    [dropbot_control_board.sch, dropbot_control_board_BOM.csv, on-board-calibration.sch, output-select.sch]
2018-07-12 Update BOM
    2 part numbers (F1 and F2) had typos and updated D4 to a part that
    is more commonly available.
    [dropbot_control_board_BOM.csv, feedback.sch, hv-square-wave-driver.sch]
2018-07-12 Fix label of A2, update netlist
    [boost-converter.sch, dropbot_control_board.kicad_pcb, dropbot_control_board.sch]
2018-07-12 Update schematic to use power ports
    [boost-converter.sch, dropbot_control_board.kicad_pcb, dropbot_control_board.sch, feedback.sch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]
2018-07-12 Update to use Sci-Bots library
    [boost-converter.sch, dropbot_control_board.kicad_pcb, dropbot_control_board.sch, dropbot_control_board_BOM.csv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]
2021-11-08 Update with kicad-helpers files
    [boost-converter.sch, dropbot_control_board.sch, feedback.sch, hv-square-wave-driver.sch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]
2021-11-10 Add manufacturing files
    [dropbot_control_board-B.Mask.gbs, dropbot_control_board-B.Paste.gbp, dropbot_control_board-B.SilkS.gbo, dropbot_control_board-BOM.csv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]
2021-11-17 Fix broken symbols and DRC tests
    [boost-converter.sch, dropbot_control_board.kicad_pcb, dropbot_control_board.sch, feedback.sch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]
2021-11-24 Fixed crlf issue
    [boost-converter.sch, dropbot_control_board.kicad_pcb, dropbot_control_board.sch, feedback.sch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]
2021-11-25 Remove "Mfg_Part_No" field (replaced by "MPN")
    [boost-converter.sch, dropbot_control_board.sch, feedback.sch, hv-square-wave-driver.sch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]
2021-11-25 Fix #2: Replace R7 with 9.1k resistor
    This should ensure that the max voltage is >140V.
    [boost-converter.sch, dropbot_control_board-BOM.csv]
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

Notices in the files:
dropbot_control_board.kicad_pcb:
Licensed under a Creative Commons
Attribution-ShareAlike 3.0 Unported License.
